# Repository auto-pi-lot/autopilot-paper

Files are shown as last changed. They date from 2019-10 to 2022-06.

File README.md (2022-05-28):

# SaundersWehr-Autopilot2019
Manuscript for Autopilot: https://www.biorxiv.org/content/10.1101/807693v1

# Building

The document is written with [tectonic](https://tectonic-typesetting.github.io/book/latest/). From the `autopilot` directory or any of its subdirectories, to build the document, run 

```bash
tectonic -X build 
```

The built document will then be located in [`autopilot/build/autopilot_v2/autopilot_v2.pdf`](autopilot/build/autopilot_v2/autopilot_v2.pdf).

**Safety Note:** To highlight the code, examples, we use [minted](http://tug.ctan.org/macros/latex/contrib/minted/minted.pdf), which requires the `shell_escape` option (specified in `Tectonic.toml`), which has the potential to run arbitrary code on your computer (we didn't purposely bundle any malware in the document).

See the blog post ["A Halfway Decent LaTeX Writing Setup"](https://jon-e.net/blog/2022/04/16/a-halfway-decent-latex-setup/) for further details and some nice QoL ideas for writing with LaTeX.

## Requirements

To compile the document, you will need

* [tectonic](https://tectonic-typesetting.github.io/book/latest/)
* [pygments](https://pygments.org/)

The fonts used in the document are mostly embedded within the .pdfs when relevant, and the open source fonts have been included in the repository, but to modify any of the source materials, you will need these fonts:

* [EB Garamond](http://www.georgduffner.at/ebgaramond/) - Bold, Italic, Regular - main body font (packaged in [`autopilot/src/garamond`](autopilot/src/garamond))
* [Fedra Mono](https://www.typotheque.com/fonts/fedra_mono) - Bold, Book, Light, Medium, Normal - Figure annotations
* [Fedra Sans Std](https://www.typotheque.com/fonts/fedra_sans) - Bold, Book, Medium, Normal, Condensed Bold, Condensed Medium - Figure axes, figure text.
* [Fira Code](https://github.com/tonsky/FiraCode) - Bold, Retina - In-text code (packaged in [`autopilot/src/fira`](autopilot/src/fira))
* [FontAwesome](https://ctan.org/pkg/fontawesome5) - Some glyphs.
* Loaded by [tufte-latex](https://github.com/Tufte-LaTeX/tufte-latex)
	* Bera Sans - Bold, Roman
	* Menlo - Regular
	* Nimbus Sans
	* PazoMath

# Document Structure

## `autopilot/`

The built document is in `autopilot/build`, and the document source is in `autopilot/src`. The `Tectonic.toml` file configures the build.

The main document text is written with:

* `_preamble.tex` - header material that defines styles, loads packages, etc.
* `autopilot.tex` - Index file that uses `\input` to combine the sections
* `sections/` - Each section is split up into multiple files within subfolders that correspond to the chapters of the paper:
	* `introduction`
	* `design`
	* `structure` - Program AStructure
	* `tests`
	* `conclusion` - Limitations and Future Directions, Glossary
* `_postamble.tex` - Document conclusion stuff.

The remaining files and folders in `src`:

* `autopilot.bib` - Bibliography for the paper exported from Zotero with Better BibTeX
* `version.tex` - A version hash that is included in the title page of the document, generated from a git hook (`.git/hooks/post-commit`).
* `figures`: The figures for the paper. Most are vectors stored as editable `.pdf` files with the flag to retain Illustrator editing features. All figures, including many not included in the first version and removed in the second version, are there. Figures containing data were mostly generated in R using [ggplot2](https://ggplot2.tidyverse.org/) and then styled (without changing the data itself) in Illustrator.
* `fira` and `garamond`: Fonts described above
* `styles`: The document style is a modified version of [tufte-latex](https://github.com/Tufte-LaTeX/tufte-latex). The source is admittedly extremely messy, I sort of hate LaTeX.
* `todo`: a separate todo document used in preparation of v2, kept for the sake of provenance.

## `code/`

The code that analyzed the data and generated the figures. Code for running the tests can be found in the autopilot paper plugin ([wiki](https://wiki.auto-pi-lot.com/index.php/Plugin:Autopilot_Paper), [repo](https://github.com/auto-pi-lot/plugin-paper)).

## `data/`

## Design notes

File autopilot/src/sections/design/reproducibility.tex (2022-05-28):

%!TEX root=../../autopilot.tex
\section{Reproducibility}
\label{sec:reproducibility}

We take a broad view on reproducibility: including not only the ability to share data and recreate experiments, but also integrating into a broader ecosystem of tools that reduces labor duplication and encourages sharing and organizing technical knowledge. For us, reproducibility means building a set of tools that make every experiment and every technique available to anyone, anywhere.

\subsection{Standardized task descriptions}

\begin{marginfigure}[-2cm]

\caption{\textbf{"Minor" details have major effects.} Proportion of mice (each point, n=4) that were successful learning the first stage of the speech task described in \citep{saundersMiceCanLearn2019} across 10 behavior boxes with variable reward sizes. A $2 \mu L$ difference in reward size had a surprisingly large effect on success rate.}
\label{fig:calibration}
\end{marginfigure}

The implementation and fine details of a behavioral experiment matter. Seemingly trivial details like milliseconds of delay between trial phases and microliters of reward volume can be the difference between a successful and unsuccessful task (Figure \ref{fig:calibration}). \textit{Reporting} those details can thus be the difference between a reproducible and unreproducible result.  Researchers also often use "auxiliary" logic in tasks---such as methods for correcting response bias---that are never completely neutral for the interpretation of results. These too can be easily omitted due to brevity or memory in plain-English descriptions of a task, such as those found in Methods sections. Even if all details of an experiment were faithfully reported, the balkanization of behavioral software into systems peculiar to each lab (or even to individuals within a lab) makes actually performing a replication of a behavior result expensive and technically challenging. Widespread use of experimental tools that are not explicitly designed to preserve every detail of their operation presents a formidable barrier to rigorous and reproducible science\citep{wallReliabilityStartsExperimental2019}.

%
\begin{marginfigure}[1.5cm]
\begin{minted}[frame=lines,fontsize=\small]{json}
{
"step_name"    : "tone_discrim",
"task_type"    : "2AFC",
"bias_mode"    : 0,
"punish_sound" : false,
"stim" : {
  "sounds" : {
    "L": {
      "duration"  : 100,
      "frequency" : 10000,
      "type"      : "tone",
      "amplitude" : 0.01},
    "R": {"...":"..."}}},
"reward": {
  "type"     : "volume",
  "volume"   : 20},
"graduation" : {
    "type"      : "accuracy",
    "threshold" : 0.75,
    "window"    : 400},
}
\end{minted}
\caption{Task parameters are stored as portable JSON, formatting has been abbreviated for clarity.}
\label{fig:params}
\end{marginfigure}%
%
%
Autopilot splits experiments into a) the \textbf{code} that runs the experiment, which is intended to be standardized and shared across implementations, and b) the \textbf{parameters} (Figure \ref{fig:params}) that define your particular experiment and system configuration. For example, two-alternative forced choice tasks have a shared structure regardless of the stimulus modality, but only your task plays pitch-shifted national anthems. This division of labor, combined with Autopilot's structured plugin system, help avoid the ubiquitous problem of rig-specific code and hard-coded variables making experimental code only useful on the single rig it was designed for --- enabling the possibility of a shared library of tasks as described in \hyperref[sec:expansion]{section \ref{sec:expansion}}%

The practice of reporting exactly the parameter description used by the software to run the experiment removes any chance for incompleteness in reporting. Because all task parameters are included in the produced data files, tasks are fully portable and can be reimplemented exactly by anyone that has comparable hardware to yours. 

\subsection{Self-Documenting Data}
\label{sec:data}

\begin{marginfigure}[1.5cm]

\caption{Example data structure. All information necessary to reconstruct an experiment is automatically stored in a human-readable HDF5 file.}
\label{fig:datastx}
\end{marginfigure}

A major goal of the open science movement is to normalize publishing well documented and clearly formatted data alongside every paper. Typically, data are acquired and stored in formats that are lab-idiosyncratic or ad-hoc, which, over time, sprout entire software libraries needed just to clean and analyze it. Idiosyncratic data formats hinder collaboration within and between labs as the same cleaning and analysis operations gain multiple, mututally incompatible implementations, duplicating labor and multiplying opportunities for difficult to diagnose bugs. Over time these data formats and their associated analysis libraries can mutate and become incompatible with prior versions, rendering years of work inaccessible or uninterpretable. In one worst-case scenario, the cleaning process unearths some critically missing information about the experiment, requiring awkward caveats in the Methods section or months of extra work redoing it. In another, the missing information or bugs in analysis code are never discovered, polluting scientific literature with inaccuracies. 

The best way to make data publishable is to avoid cleaning data altogether and \textit{design good data hygiene practices into the data acquisition process.} Autopilot automatically stores all the information required to fully reconstruct an experiment, including any changes in task parameters or code version that happen throughout training as the task is refined.

Autopilot data is stored in \href{https://support.hdfgroup.org/HDF5/whatishdf5.html}{HDF5} files, a hierarchical, high-performance file format. HDF5 files support metadata throughout the file hierarchy, allowing annotations to natively accompany data. Because HDF5 files can store nearly all commonly used data types, data from all collection modalities---trialwise behavioral data, continuous electrophysiological data, imaging data, etc.---can be stored together from the time of its acquisition. Data is always stored with the full conditions of its collection, and is ready to analyze and publish immediately (Figure \ref{fig:datastx}). No Autopilot-specific scripts are needed to import data into your analysis tool of choice---anything that can read HDF5 files can read Autopilot data\sidenote{Though our \texttt{Subject} class provides a simplified interface to access and manipulate Autopilot data}. 

As of v0.5.0, we have built a formal data modeling system into Autopilot, allowing for unified declaration of data for experimental subjects, task parameters, and resulting data with verifiable typing and human-readable annotations. These abstract data models can be used with multiple storage interfaces, paving the way for export to, for example, the Neurodata Without Borders standard\citep{rubelNWBAccessibleData2019}, further enabling Autopilot data to be immediately incorporated into existing processing pipelines (see section \ref{sec:datamodel}).

\subsection{Testing \& Continuous Integration}

Open-source scientific software does away with prior limitations to access and inspection imposed by proprietary tools. It also exposes the research process to bugs in software written by semi-amateurs that can yield errors in the resulting data, analysis, and interpretation\citep{soergelRampantSoftwareErrors2015,eklundClusterFailureWhy2016a,bhandarineupaneCharacterizationLeptazolinesPolar2019,millerScientistNightmareSoftware2006}. Autopilot tries to bring best practices in software development to experimental software, including a set of automated tests for continuous integration. 

We are still formalizing our contribution process, and our tests are still far from achieving full coverage\sidenote[][-3.25cm]{Coverage statistics for Autopilot are available on coveralls.io at \url{https://coveralls.io/github/auto-pi-lot/autopilot}}, but we currently require tests and documentation for all new code added to the library. Writing good tests is hard, and we are in the process of building a set of hardware simulators and test fixtures to ease contribution.  

Tests are effectively provable statements about how a program functions (Figure \ref{fig:tests}), which are particularly important for a library that aspires to be baseline lab infrastructure like Autopilot. Tests make it possible to use and contribute to the library with confidence: all tests are run on every commit, making it possible to determine if some new contribution breaks existing code without manually reading and testing every line. As we work to complete our test coverage, we hope to provide researchers with a tool that they can trust and elevates the verifiability of scientific results at large.

\begin{marginfigure}[-7cm]
\begin{minted}[frame=lines,fontsize=\small]{python}
def test_set_gpio():
    """
    The `set` method of a Digital_Out
    object sets the pin state
    """
    pin = Digital_Out(pin=17)

    # Turn GPIO pin on
    pin.set(True)
    assert pin.state == True

    # Turn GPIO pin off
    pin.set(False)
    assert pin.state == False
\end{minted}
\caption{A test like \texttt{test\_set\_gpio} is a provable statement about the functionality of a program, in this case that "the \texttt{Digital\_Out.set()} method sets the state of a GPIO pin."}
\label{fig:tests}
\end{marginfigure}

\subsection{Expense}
\label{sec:expense}

Autopilot is an order of magnitude less expensive than comparable behavioral systems (Table \ref{tab:cost}). We think the expense of a system is important for two reasons: scientific equity and statistical power. 

The distribution of scientific funding is highly skewed, with a large proportion of research funding concentrated in relatively few labs\citep{katzBiomedicalEliteInequality2017}. Lower research costs benefit all scientists, but lower instrumentation costs directly increase the accessibility of state-of-the-art experiments to labs with less funding. Since well-funded labs also tend to be concentrated at a few (well-funded) institutions, lower research costs also broaden the base of scientists outside traditional research institutions that can stay at the cutting edge\citep{ashkenasEvenAffirmativeAction2017,clausetSystematicInequalityHierarchy2015,pearceExpandingEquitableAccess2019}.
\clearpage%
%
\begin{marginfigure}[0.5cm]

\caption{When comparing a value across groups, eg. a genetic knockout vs. wildtype, even a modest intra-animal (or, more generally, intra-cluster) correlation (ICC) causes the false positive rate to be far above the nominal $\alpha = 0.05$. Shown are false positive rates for simulated data with various numbers of "cells" recorded for comparisons between two groups of 5 animals each with a real effect size of 0. We note that 741 simultaneously recorded cells were reported in \citep{junFullyIntegratedSilicon2017} and a mean ICC of 0.19 across 18 neuroscientific datasets was reported in \citep{aartsSolutionDependencyUsing2014}}
\label{fig:icc}
\end{marginfigure}%
%
Neuroscience also stands to benefit from the lessons learned from the replication crisis in Psychology\citep{shroutPsychologyScienceKnowledge2018}. In neuroscience, underpowered experiments are the rule, rather than the exception\citep{buttonPowerFailureWhy2013}. Statistical power in neuroscience is arguably even worse than it appears, because large numbers of observations (eg. neural recordings) from a small number of animals are typically pooled, ignoring the nested structure of observations collected within individual animals. Increasing the number of cells recorded from a small number of animals dramatically increases the likelihood of Type I errors (Figure \ref{fig:icc})---indeed, for values of within-animal correlation typical of neuroscientific data, high numbers of observations make Type I errors more likely than not\citep{aartsSolutionDependencyUsing2014}. For this reason, perhaps paradoxically, recent technical advances in multiphoton imaging and silicon-probe recordings will actually make statistical rigor in neuroscience \textit{worse} if we don't use analyses that account for the multilevel structure of the data and correspondingly record from the increased number of animals that they require.

Although the expense of multi-photon imaging and high-density electrophysiology will always impose an experimental bottleneck, behavioral training time is often the greater determinant of study sample size. Typical behavioral experiments require daily training sessions often carried out over weeks and months, while far fewer imaging or electrophysiology sessions are carried out per animal.  Training large cohorts of animals in parallel is thus the necessary basis of a well-powered imaging or electrophysiology experiment.

\begin{table}
\caption{\textbf{Cost for Basic 2AFC System}\\
\noindent"Nosepoke" includes a solenoid valve, IR sensor, water tube, LED, housing, and any necessary driver PCBs. For PyControl and Autopilot, we included the cost of one \href{https://wiki.auto-pi-lot.com/index.php/Lee_LHDA0531115H}{Lee LHDA0531115H} solenoid valve per nosepoke (\$63.35). For PyControl, we estimated a typical USB hub with 5 ports to control 5 pyControl systems from one computer. We note that the Bpod and PyControl systems both include cost of assembly for the control CPUs and nosepokes, but also that Autopilot does not require assembly for its control CPU and its default nosepoke is a snap-together 3D printed part and PCB without surface mounted components that can be assembled by an amateur in roughly half an hour.}
\label{tab:cost}
\noindent\begin{tabularx}{\linewidth}{XRRR}\toprule
& Autopilot & pyControl & Bpod  \\
\midrule
Behavior CPU & 
\href{https://www.adafruit.com/product/4292}{\texttt{\$45}} & 
\href{https://open-ephys.org/pycontrol/pycontrol}{\texttt{\$270}} & 
\href{https://sanworks.io/shop/viewproduct?productID=1024}{\texttt{\$925}}\\
Nosepoke (3x) & 
\texttt{\$216} & 
\href{http://www.open-ephys.org/store/pycontrol-peripherals}{\texttt{\$369}} & 
\href{https://sanworks.io/shop/viewproduct?productID=1009}{\texttt{\$810}} \\
\textbf{Total for One} & 
\textbf{\texttt{\$261}} & 
\textbf{\texttt{\$639}} & 
\textbf{\texttt{\$1735}}\\
\midrule
Five Systems & 
\texttt{\$1305} & 
\texttt{\$3195} & 
\texttt{\$8675} \\
Host CPU(s) & 
\texttt{\$1000} & 
\texttt{\$1000} & 
\texttt{\$5000} \\
\textbf{Total for Five} & 
\textbf{\texttt{\$2305}} & 
\textbf{\texttt{\$4195}} & 
\textbf{\texttt{\$13625}} \\
\midrule
\textbf{Total for Ten} & 
\textbf{\texttt{\$3610}} & 
\textbf{\texttt{\$8390}} & 
\textbf{\texttt{\$27350}} \\
\bottomrule
\end{tabularx}
\end{table}

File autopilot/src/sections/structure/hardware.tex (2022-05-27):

%!TEX root=../../autopilot.tex
\section{Hardware}
\label{sec:hardware}

The Raspberry Pi can interface with nearly all common hardware, and has an \href{https://www.raspberrypi.org/help/}{extensive collection} of \href{https://elinux.org/RPi_Guides}{guides}, \href{https://elinux.org/RPi_Tutorials}{tutorials}, and an active \href{https://www.raspberrypi.org/forums/}{forum} to support users implementing new hardware. There is also an enormous amount of existing hardware for the Raspberry Pi, including \href{https://www.hifiberry.com/}{sound cards}, \href{https://www.adafruit.com/product/2348}{motor controllers}, \href{https://www.digikey.com/product-detail/en/raspberry-pi/SENSE-HAT/1690-1013-ND/6196429}{sensor arrays}, \href{https://www.seeedstudio.com/Raspberry-Pi-High-Precision-AD-DA-Board-p-2765.html}{ADC/DACs}, and \href{https://www.digikey.com/product-detail/en/pimoroni-ltd/PIM369/1778-1221-ND/9521981}{touchscreen displays}, largely eliminating the need for a separate ecosystem of purpose-built hardware (Table \ref{tab:periphs}). 

\begin{margintable}[-0.75cm]
\caption{
\textbf{Cost of common peripherals.} The native hardware of the Raspberry Pi, low-level hardware control of Autopilot, and availability of inexpensive off-the-shelf components compatible with the raspi make most custom-built peripherals unnecessary.}
\label{tab:periphs}
\noindent\begin{tabularx}{\linewidth}{Rll}
\toprule
\textbf{Device} & Raspi & Bpod \\
\midrule
HiFiBerry DAC2 Pro & \href{https://www.hifiberry.com/shop/boards/hifiberry-dac2-pro/}{\$45} &  \href{https://sanworks.io/shop/viewproduct?productID=1032}{\$445}\\
ADC & \href{https://thepihut.com/products/high-precision-adc-hat-for-raspberry-pi-10-channel-32-bit}{\$30} & \href{https://sanworks.io/shop/viewproduct?productID=1021}{\$495}\\
I2C & \$0 & \href{https://sanworks.io/shop/viewproduct?productID=1019}{\$225} \\
Ethernet & \$0 & \href{https://sanworks.io/shop/viewproduct?productID=1025}{\$285} \\
Rotary Encoder & \$0 &  \href{https://sanworks.io/shop/viewproduct?productID=1022}{\$145}\\
\bottomrule
\end{tabularx}
\end{margintable}

\begin{marginfigure}[0cm]
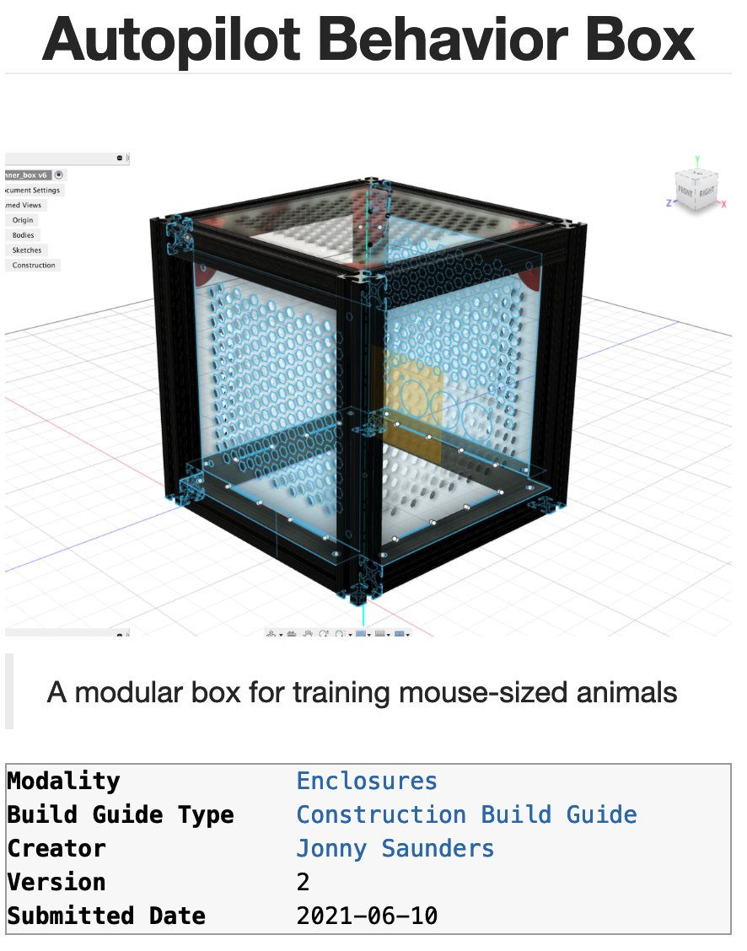
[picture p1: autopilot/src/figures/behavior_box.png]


\caption{Two examples of parts with assembly guides available on the autopilot wiki: A modular \href{https://wiki.auto-pi-lot.com/index.php/Autopilot_Behavior_Box}{behavior box} with magnetic snap-in panels (top), and a \href{https://wiki.auto-pi-lot.com/index.php/Autopilot_Tripoke}{three-nosepoke panel} (bottom).}
\label{fig:pokeport}
\end{marginfigure}%

Autopilot controls hardware with an extensible inheritance hierarchy of Python classes intended to be built into a library of hardware controllers analogously to tasks. Autopilot uses \href{http://abyz.me.uk/rpi/pigpio/}{pigpio} to interact with its GPIO pins, giving Autopilot $5 \mu s$ measurement precision and enabling protocols that require high precision (such as Serial, PWM, and I2C) for nearly all of the pins.  Currently, Autopilot also has a family of objects to control cameras (both the \href{https://docs.auto-pi-lot.com/en/latest/hardware/cameras.html\#autopilot.hardware.cameras.PiCamera}{Raspberry Pi Camera} and \href{https://docs.auto-pi-lot.com/en/latest/hardware/cameras.html\#autopilot.hardware.cameras.Camera_Spinnaker}{high-speed GENICAM-compliant} cameras), i2c-based \href{https://docs.auto-pi-lot.com/en/latest/hardware/i2c.html\#autopilot.hardware.i2c.I2C_9DOF}{motion} and \href{https://docs.auto-pi-lot.com/en/latest/hardware/i2c.html\#autopilot.hardware.i2c.MLX90640}{heat} sensors, and \href{https://docs.auto-pi-lot.com/en/latest/hardware/usb.html\#autopilot.hardware.usb.Wheel}{USB mice}.  In the \hyperref[sec:future]{future} we intend to improve performance further by replacing time-critical hardware operations with low-level interfaces written in Rust.

\begin{table}[b]
\caption[][0cm]{Specifications of reviewed behavior hardware. BPod's state machine uses the Teensy 3.6 microcontroller, and PyControl uses the Micropython Pyboard.}
\label{hwtab}
\begin{tabularx}{\linewidth}{Rp{3.5cm}p{2cm}p{2cm}}\toprule
& \href{https://www.raspberrypi.org/products/raspberry-pi-4-model-b/specifications/}{\textbf{Raspberry Pi 4B}} & \href{https://www.pjrc.com/teensy/techspecs.html}{\textbf{Teensy 3.6}} & \href{https://micropython.org/}{\textbf{pyboard}}\\
\midrule
CPU Clock & 1.5GHz & 180MHz & 168MHz \\
CPU Cores & 4 & 1 & 1 \\
Architecture & ARMv8-A, 64-bit & ARMv7 32-bit & ARMv7 32-bit \\
RAM Size & 2, 4, or 8GB & 256KB & 192KB\\
Storage & MicroSD (any size) & 1024KB & 1024KB \\
GPU & Broadcom VideoCore VI & \textcolor{red}{---} & \textcolor{red}{---} \\
GPIO Pins & 40 & 58 & 29 \\
USB Ports & 2x USB 2.0, 2x USB 3.0  & 2x USB 2.0 & 1x USB 2.0 \\
Ethernet & 1Gbps & 100Mbps & \textcolor{red}{---} \\
WiFi & 2.4/5 GHz b/g/n/ac & \textcolor{red}{---} & \textcolor{red}{---} \\
Camera & 15-pin Serial Interface & \textcolor{red}{---} & \textcolor{red}{---} \\
Bluetooth & \checkmark & \textcolor{red}{---} & \textcolor{red}{---} \\
\end{tabularx}
\end{table}

To organize and make available the vast amount of contextual knowledge needed to build and use experimental hardware, we have made a densely linked and publicly editable \href{https://wiki.auto-pi-lot.com/index.php/Autopilot_Wiki}{semantic wiki}. The Autopilot wiki contains, among others, reference information for \href{https://wiki.auto-pi-lot.com/index.php/Parts}{off-the-shelf parts}, schematics for \href{https://wiki.auto-pi-lot.com/index.php/2D_CAD}{2D} and \href{https://wiki.auto-pi-lot.com/index.php/3D_CAD}{3D}-printable components, and \href{https://wiki.auto-pi-lot.com/index.php/Guides}{guides} for building experimental apparatuses and custom parts. The wiki combines unrestrictive freeform editing with structured, computer-readable \href{https://www.semantic-mediawiki.org/wiki/Semantic_MediaWiki}{semantic properties}, and we have defined a collection of \href{https://wiki.auto-pi-lot.com/index.php/Special:CategoryTree?target=Hardware&mode=categories&namespaces=&title=Special%3ACategoryTree}{schemas} for commonly documented items coupled with \href{https://wiki.auto-pi-lot.com/index.php/Special:Forms}{submission forms} for ease of use. For example, the wiki page for the \href{https://wiki.auto-pi-lot.com/index.php/Lee_LHDA0531115H}{Lee Company solenoid} we use has fields from a generic \href{https://wiki.auto-pi-lot.com/index.php/Category:Part}{Part} schema like a datasheet, price, and voltage, but also that it's a 3-way, normally-closed \href{https://wiki.auto-pi-lot.com/index.php/Category:Solenoid}{solenoid}. 

The wiki's blend of structure and freedom breaks apart typically monolithic hardware documentation into a collaborative, multimodal technical knowledge graph. Autopilot can access the wiki through its \href{https://docs.auto-pi-lot.com/en/latest/guide/plugins.html\#the-wiki-api}{API}, and we intend to tighten their integration over time, including automatic configurations for common parts, usage and longevity benchmarks, detecting mutually incompatible parts, and automatically resolving any additional plugins or dependencies needed to use a part.

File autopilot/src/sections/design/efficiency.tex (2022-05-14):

%!TEX root=../../autopilot.tex
\section{Efficiency}
\label{sec:efficiency}

Though it is a single board, the Raspberry Pi operates more like a computer than a microcontroller. It most commonly runs a custom Linux distribution, Raspbian, allowing Autopilot to use Python across the whole system. Using an interpreted language like Python running on Linux has inherent performance drawbacks compared to compiled languages running on embedded microprocessors. In practice these drawbacks are less profound than they appear on paper: Python's overhead is negligible on modern processors\sidenote{and improvements to CPython in \href{https://docs.python.org/3.11/whatsnew/3.11.html\#faster-cpython}{Python 3.11} and onwards will bring overhead close to zero\citep{andersonGuidoVanRossum2021}}, jitter and performance can be improved by wrapping \hyperref[sec:lowlevel]{compiled code}, etc. While we view the gain in accessibility and extensibility of a widely used high-level language like Python as outweighing potential performance gains from using a compiled language, Autopilot is nevertheless designed to maximize computational efficiency.

\subsection{Concurrency}

\begin{marginfigure}[2cm]

\caption{A single-threaded program executes all operations sequentially, using a single process and cpu core.}
\label{fig:singlethread}
\end{marginfigure}

Most behavioral software is single-threaded (Figure \ref{fig:singlethread}), meaning the program will only perform a single operation at a time. If the program is busy or waiting for an input, other operations are blocked until it is finished.

Autopilot distributes computation across multiple processes and threads to take advantage of the Raspberry Pi's four CPU cores. Most operations in Autopilot are executed in \textbf{threads}. Specifically, Autopilot spawns separate threads to process messages and events, an architecture described more fully in \hyperref[sec:networking]{section \ref*{sec:networking}}. Threading does not offer true concurrency\sidenote{See David Beazley's  \href{http://www.dabeaz.com/python/UnderstandingGIL.pdf}{`Understanding the Global Interpreter Lock'} and associated \href{http://www.dabeaz.com/GIL/gilvis/index.html}{visualizations}.}, but does allow Python to distribute computational time between operations so that, for example, waiting for an event does not block the rest of the program, and events are not missed because the program is busy (Figure \ref{fig:multithread}).

\begin{marginfigure}[0.25cm]

\caption{A multi-threaded program divides computation time of a single process and cpu core across multiple operations so that, for example, waiting for input doesn't block other operations.}
\label{fig:multithread}
\end{marginfigure}

Critical operations that are computationally intensive or cannot be interrupted are given their own dedicated \textbf{processes}. Linux allows individual cores of a processor to be reserved for single processes, so individual Raspberry Pis are capable of running four truly parallel processing streams. For example, all Raspberry Pis in an Autopilot swarm create a messaging client to handle communication between devices which runs on its own processor core so no messages are missed. Similarly, if an experiment requires sound delivery, a realtime \hyperref[sec:stim]{sound engine} in a separate process (Figure \ref{fig:multiprocess}) also runs on its own core.

\begin{marginfigure}[0.1cm]
 
 \caption{A multi-process program is truly concurrent, allowing multiple cpu cores to operate in parallel.}
 \label{fig:multiprocess}
\end{marginfigure}

Since even moderately complex experiments can consume more resources than are available on a single processor, the topmost layer of concurrency in Autopilot is to use additional \textbf{computers}. Autopilot uses the Raspberry Pi as a low-cost hardware controller, but only its GPIO control system is unique to them: the rest of the code can be used on any type of computer, so computationally expensive or GPU-intensive operations can be offloaded to any number of high performance machines. Computers divide labor \textit{autonomously} (see \ref{sec:message_handling} and \ref{sec:agents} ), so for example one computer running a task can send and receive messages from another running the GUI and plots, but does not \textit{depend} on that input as it would in a system that couples a microcontroller with a managing computer. The ability to coordinate multiple, autonomous computers with heterogeneous responsibilities and capabilities in a shared task is Autopilot's definitive design decision.

\subsection{Leveraging Low-Level Libraries}
\label{sec:lowlevel}

\begin{margintable}[1.85cm]
\caption{A few libraries Autopilot uses}
\label{tab:libraries}
\noindent\begin{tabularx}{\linewidth}{rX}
\toprule
 \textbf{\href{http://jackaudio.org/}{jack}} & realtime audio \\
 \textbf{\href{http://abyz.me.uk/rpi/pigpio/index.html}{pigpio}} & GPIO control \\
 \textbf{\href{http://zeromq.org/}{ZeroMQ}} & networking \\
 \textbf{\href{https://www.qt.io/}{Qt}} & GUI \\
 \bottomrule
\end{tabularx}
\end{margintable}

Autopilot uses Python as a "glue" language, where it wraps and coordinates faster low-level compiled code\citep{vanrossumGlueItAll1998}.  
Performance-critical components of Autopilot are thin wrappers around fast C libraries (Table \ref{tab:libraries}). As Autopilot's API matures, we intend to replace any performance-limiting Python code like its sound server and networking operations with compiled code exposed to python with tools like the C Foreign Function Interface (\href{https://cffi.readthedocs.io/en/latest/index.html}{CFFI}).

Since Autopilot coordinates its low-level components in parallel rather putting everything inside one "main loop," Autopilot actually has \textit{better} temporal resolution than  single-threaded systems like Bpod or pyControl, despite the realtime nature of their dedicated processors (Table \ref{tab:precision}).

\begin{margintable}
\caption{Using pigpio as a dedicated I/O process gives autopilot greater measurement precision}
\label{tab:precision}
\noindent\begin{tabularx}{\linewidth}{rR}\toprule
& Precision \\
\midrule
Autopilot (\href{http://abyz.me.uk/rpi/pigpio/pigpiod.html}{pigpio}) & $5\mu s$ \\
\href{https://github.com/sanworks/Bpod_StateMachine_Firmware/blob/059d1e9195f5bb7d0d5cd7b33f56342eb5a3a55c/Dev/StateMachineFirmware/StateMachineFirmware.ino\#L196}{Bpod} & $100\mu s$ \\
\href{https://github.com/pyControl/code/blob/28cf5ea28ca2764aeea829eba148adfa5239254a/pyControl/framework.py\#L228}{pyControl} & $1000\mu s$ \\
\bottomrule
\end{tabularx}
\end{margintable}

\subsection{Caching}

Finite-state machines are only aware of the current state and the events that transition it to future states. They are thus incapable of exploiting the often predictable structure of behavioral tasks to precompute future states and precache stimuli. Further, to change task parameters between trials (eg. changing the rewarded side in a two-alternative forced-choice task), state machines need to be fully reconstructed and reuploaded to the device that runs them each time.

Autopilot precomputes and caches as much as possible. Rather than wait "inside" a state, Autopilot prepares each of the next possible events and saves them for immediate execution when the appropriate trigger is received. Static stimuli are prepared once at the beginning of a behavioral session and stored in memory. Before their presentation, they are buffered to minimize latency.

By providing full low-level documentation, we let researchers choose the balance between ease of use and performance themselves: it's possible to just call a sound's \texttt{\href{https://docs.auto-pi-lot.com/en/latest/stim/sound/base.html\#autopilot.stim.sound.base.Jack_Sound.play}{play()}} method, explicitly buffer it with its \texttt{\href{https://docs.auto-pi-lot.com/en/latest/stim/sound/base.html\#autopilot.stim.sound.base.Jack_Sound.buffer}{buffer()}} method, or generate samples on the fly with its \texttt{\href{https://docs.auto-pi-lot.com/en/latest/stim/sound/base.html\#autopilot.stim.sound.base.Jack_Sound.play_continuous}{play\_continuous()}} method. Similarly, messages can be sent with a networking node's \texttt{\href{https://docs.auto-pi-lot.com/en/latest/networking/node.html\#autopilot.networking.node.Net_Node.send}{send()}} method, or prepared beforehand by explicitly making a \texttt{\href{https://docs.auto-pi-lot.com/en/latest/networking/message.html\#autopilot.networking.message.Message}{Message}} and calling its \texttt{\href{https://docs.auto-pi-lot.com/en/latest/networking/message.html\#autopilot.networking.message.Message.serialize}{serialize()}} method.

\vspace{16pt}

Autopilot's efficient design lets it access the best of both worlds---the speed and responsiveness of compiled code on dedicated microprocessors and the accessibility and flexibility of interpreted code.

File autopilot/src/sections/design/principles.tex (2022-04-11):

%!TEX root=../../autopilot.tex
\newthought{Autopilot distributes experiments} across a network of Raspberry Pis,\sidenote{\href{https://www.raspberrypi.org/products/raspberry-pi-4-model-b/}{Raspberry Pi model 4B}, see \hyperref[hwtab]{Table \ref*{hwtab}}} a type of inexpensive single-board computer.

\vspace{12pt}

\textbf{Autopilot has three primary design principles:}

\begin{enumerate}
    \item \hyperref[sec:efficiency]{\textbf{Efficiency}} - Autopilot should minimize computational overhead and maximize use of hardware resources.
    \item \hyperref[sec:flexibility]{\textbf{Flexibility}} - Autopilot should be transparent in all its operations so that users can expand it to fit their existing or desired use-cases. Autopilot should provide clear points of modification and expansion to reduce local duplication of labor to compensate for its limitations.
    \item \hyperref[sec:reproducibility]{\textbf{Reproducibility}} - Autopilot should maximize system transparency and minimize the potential for the black-box of local reprogramming. Autopilot should maximize the information it stores about its operation as part of normal data collection.
\end{enumerate}

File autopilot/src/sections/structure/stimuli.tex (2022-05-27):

%!TEX root=../../autopilot.tex
\section{Stimuli}
\label{sec:stim}

\begin{marginfigure}[0.45cm]
\begin{pythoncode*}{
label= \texttt{An Autopilot Tone},
frame=lines,
linenos=false}

my_tone = sounds.Tone(
    frequency = 500,
    duration  = 200)
my_tone.play()
\end{pythoncode*}
\caption{Autopilot stimuli are parametrically defined and inherit all the playback logic that makes them easy to integrate in tasks}
\label{fig:tone}
\end{marginfigure}

A hardware object would control a speaker, whereas stimulus objects are the individual sounds that the speaker would play. Like tasks and hardware, Autopilot makes stimulus generation portable between users, and is released with a family of common sounds like tones, noises, and sounds from files. The logic of sound presentation is contained in an inherited metaclass, so to program a new stimulus a user only needs to describe how to generate it from its parameters (Figure \ref{fig:tone}).  Sound stimuli are better developed than visual stimuli as of v0.5.0, but we present a proof-of-concept visual experiment (Section \ref{sec:gonogo}) using \href{https://www.psychopy.org/}{psychopy}\citep{peircePsychoPy2ExperimentsBehavior2019}.

Autopilot controls the realtime audio server \href{http://jackaudio.org/}{jack} from an independent Python process that dumps samples directly into jack's buffer (Figure \ref{fig:soundpath}), giving it a trigger-to-playback latency very near the theoretical minimum (Section \ref{sec:soundlatency}). Sounds can be pre-buffered in memory or synthesized on demand to play continuous sounds. Because the realtime server is independent from the logic of sound synthesis and storage, stimuli can be controlled independently from different threads without interrupting audio or dropping frames.

\begin{marginfigure}[0cm]

\caption{Our sound server keeps audio samples buffered until a \texttt{.play()} method is called, and then dumps them directly into the jack audio daemon.}
\label{fig:soundpath}
\end{marginfigure}

We use the \href{https://www.hifiberry.com/shop/boards/hifiberry-amp2/}{Hifiberry Amp 2}, a combined sound card and amplifier, which is capable of 192kHz/24Bit audio playback. Autopilot and Jack can output to any sound hardware, however, including the builtin audio of the Raspberry Pi if fidelity isn't important. There are no external video cards for the Raspberry Pi 4b\sidenote[][0cm]{though the Raspberry Pi compute module has a \href{https://web.archive.org/web/20220506011247/https://www.jeffgeerling.com/blog/2020/external-gpus-and-raspberry-pi-compute-module-4}{PCI lane that supports GPUs}.}, but its embedded video card is capable of presenting video and visual stimuli (Section \ref{sec:gonogo}) especially if the other computationally demanding parts of the task are distributed to other Raspberry Pis (Section \ref{sec:topology}). If greater video performance is needed, Autopilot is capable of running on typical desktops as well as other single-board computers with GPUs (as we did with the Nvidia Jetson in \citep{kaneRealtimeLowlatencyClosedloop2020a}).

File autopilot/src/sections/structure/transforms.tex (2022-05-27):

%!TEX root=../../autopilot.tex
\section{Transforms}
\label{sec:transforms}

In v0.3.0, we introduced the \texttt{transform} module, a collection of tools for transforming data. The raw data off a sensor is often not in itself useful for performing an experiment: we want to compare it to some threshold, extract positions of objects in a video feed, and so on. Transforms are like building blocks, each performing some simple operation with a standard object structure, and then composed into a pipeline (Figure \ref{fig:transform_example}). Pipelines are portable, and can be created on the fly from a JSON representation of their arguments, so it's easy to offload expensive operations to a more capable machine for distributed realtime experimental control (See \citep{kaneRealtimeLowlatencyClosedloop2020a}). 

\begin{marginfigure}[-8cm]

\end{marginfigure}

\begin{marginfigure}[-3.5cm]
\begin{pythoncode*}{
label= \texttt{Transform - DLC Live!},
frame=lines,
linenos=false}
from autopilot import transform as t
# track points on a human body
dlc = t.image.DLC(
    model_zoo="full_human")
# select one of the knees
dlc += t.selection.DLCSlice(
    select="knee2")
# Test if it's in an ROI
dlc += t.logical.Condition(
    minimum=(0,0),
    maximum=(128,128))

# Process frames with the pipeline
# set pin High if knee2 in ROI
while True:
    pin.set(dlc.process(
        cam.q.get()))
\end{pythoncode*}
\caption{Transforms can be chained together (here with the in-place addition operator \texttt{+=}) to make pipelines that encapsulate the logical relationship between some input and a desired output. Here \texttt{pin} is a \href{https://docs.auto-pi-lot.com/en/latest/hardware/gpio.html\#autopilot.hardware.gpio.Digital_Out}{Digital\_Out} object, and \texttt{cam} is a \href{https://docs.auto-pi-lot.com/en/latest/hardware/cameras.html\#autopilot.hardware.cameras.PiCamera}{PiCamera} with \texttt{queue} enabled.}
\label{fig:transform_example}

\end{marginfigure}

In addition to computing derived values, we use transforms in a few ways, including

\begin{itemize}
\item \textbf{Bridging Hardware} --- Different hardware devices use different data types, units, and scales, so transforms can \href{https://docs.auto-pi-lot.com/en/latest/transform/units.html\#autopilot.transform.units.Rescale}{rescale} and convert values to make them compatible.
\item \textbf{Integrating External Tools} --- The number of exciting analytical tools for realtime experiments keep growing, but in practice they can be hard to use together. The transform module gives a scaffolding for writing wrappers around other tools and exposing them to each other in a shared framework, as we did with DeepLabCut-Live\citep{kaneRealtimeLowlatencyClosedloop2020a}, making closed-loop pose tracking available to the rest of Autopilot's ecosystem. We don't need to rally thousands of independent developers to agree to write their tools in a shared library, instead transforms make wrapping them easy.
\item \textbf{Extending Objects} --- Transforms can be used to augment existing objects and create new ones. For example, a \href{https://docs.auto-pi-lot.com/en/latest/hardware/i2c.html#autopilot.hardware.i2c.I2C_9DOF}{motion sensor} uses the \href{https://docs.auto-pi-lot.com/en/latest/transform/geometry.html\#autopilot.transform.geometry.Spheroid}{spheroid} transform to calibrate its accelerometer, and the \href{https://docs.auto-pi-lot.com/en/latest/transform/timeseries.html\#autopilot.transform.timeseries.Gammatone}{gammatone filter}\sidenote[][0.25cm]{a thin wrapper around \href{https://docs.scipy.org/doc/scipy/reference/generated/scipy.signal.gammatone.html}{scipy's \texttt{signal.gammatone}}} extends the \href{https://docs.auto-pi-lot.com/en/latest/stim/sound/sounds.html\#autopilot.stim.sound.sounds.Noise}{Noise} sound to make a gammatone \href{https://docs.auto-pi-lot.com/en/latest/stim/sound/sounds.html\#autopilot.stim.sound.sounds.Gammatone}{filtered noise} sound.
\end{itemize}

Like Tasks and Hardware, the transform module provides a scaffolding for writing reference implementations of algorithms commonly needed for realtime behavioral experiments. For example, neuroscientists often want to quickly measure a research subject's velocity or orientation, which is possible with inexpensive inertial motion sensors (IMUs), but since anything worth measuring will be swinging the sensor around with wild abandon the readings first need to be rotated back to a geocentric coordinate frame. Since the readings from an accelerometer are noisy, we found a few whitepapers describing using a Kalman filter for fusing the accelerometer and gyroscope data for a more accurate orientation estimate (\citep{abyarjooImplementingSensorFusion2015b,patonisFusionMethodCombining2018a}), but couldn't find an implementation. We \href{https://docs.auto-pi-lot.com/en/latest/_modules/autopilot/transform/geometry.html\#IMU_Orientation}{wrote one} and integrated it into the IMU class (Figure \ref{fig:imu}). Since it's an independent transform, it's available to anyone even if they use nothing else from Autopilot.

\begin{marginfigure}[-1.5cm]
\begin{pythoncode*}{
label=Geocentric Velocity,
frame=lines,
linenos=false
}
# rotate input in x and y
# by some pitch and roll
reorient = t.geometry.Rotate(
    dims='xy') 
# select the z axis
reorient += t.selection.Slice(
    select=2)
# remove gravity
reorient += t.math.Add(
    -9.8)

# using I2C_9DOF...
angle = imu.rotation
z_accel = reorient.process(
    imu._acceleration, angle)
\end{pythoncode*}
\caption{Using the \href{https://docs.auto-pi-lot.com/en/latest/_modules/autopilot/transform/geometry.html\#IMU_Orientation}{IMU\_Orientation} transform built into the IMU's \texttt{rotation} property, a processing chain to reorient the accelerometer reading and subtract gravity for geocentric z-axis acceleration.}
\label{fig:imu}
\end{marginfigure} 

Transforms were made to be composed, so we broke it into independent sub-operations: A \href{https://docs.auto-pi-lot.com/en/latest/transform/timeseries.html\#autopilot.transform.timeseries.Kalman}{Kalman} filter, \href{https://docs.auto-pi-lot.com/en/latest/transform/geometry.html\#autopilot.transform.geometry.Rotate}{rotation}, and a \href{https://docs.auto-pi-lot.com/en/latest/transform/geometry.html\#autopilot.transform.geometry.Spheroid}{spheroid correction} to calibrate accelerometers. Then we combined it with the DLC-Live transform for a fast but accurate motion estimate from position, velocity, and acceleration measurements from three independent sensors. Since each step of the transformation is exposed in a clean API, it was straightforward to \href{https://github.com/auto-pi-lot/autopilot-plugin-parallax/blob/759dbb382b90a99f71edf5070772ac18555b67dd/kalman\_position.py}{extend the Kalman filter} to accomodate the the wildly different sampling rates of the camera and IMU. It's still got its quirks, but that's the purpose of plugins --- to make the code \href{https://wiki.auto-pi-lot.com/index.php/Plugin:Parallax}{available and documented} without formally integrating it in the library. 

\clearpage

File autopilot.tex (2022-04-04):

% !TEX options=--shell-escape
\documentclass[nohyper, justified, notitlepage, marginals=raggedright,twoside=false,debug]{tufte-autopilot}

%% Package imports
\usepackage{microtype}
\usepackage{amsmath}
\usepackage{booktabs}
\usepackage{xspace}
\usepackage{units}
\usepackage{makeidx}
\usepackage[framemethod=tikz]{mdframed}% http://ctan.org/pkg/mdframed
\usepackage{lipsum}
\usepackage{listings}
\usepackage{minted}
%\usepackage[usenames, svgnames]{xcolor}
\usepackage[colorlinks = true,
            urlcolor = DarkOrchid,
            citecolor = DarkOrchid,
            backref= section]{hyperref}
\usepackage{tikz}
\usepackage{verbatim}
\usepackage{tabularx}
\usepackage{enumitem} % pause itemize env
\usepackage[font=footnotesize, labelfont=bf]{caption}
\usepackage{ulem}     % strikeouts
%\usepackage[english]{babel}
\usepackage[autostyle, english=american]{csquotes} % styling smart quotes
\usepackage[titletoc]{appendix} % add appendices
%\usepackage{scrextend}
%\usepackage{etoolbox}
%\usepackage[toc, automake=true]{glossaries}
\usepackage{listliketab}
%\usepackage{authblk}
%\usepackage{abstract} % to get saythanks
\usepackage{ fontawesome }

\usetikzlibrary{tikzmark}
\usetikzlibrary{calc}
\usetikzlibrary{positioning}
\usetikzlibrary{decorations.pathreplacing}

%% Imports with customizations
% For graphics / images
\usepackage{graphicx}
\setkeys{Gin}{width=\linewidth,totalheight=\textheight,keepaspectratio}
\graphicspath{{graphics/}}

\usepackage{fancyvrb}
\fvset{fontsize=\normalsize}

\titlespacing*{\chapter}{0pt}{-10pt}{0pt}
%\titlespacing{\section}{0pt}{30pt}{0pt}

%% Import extra shit from overleaf doc - see what's necessary.
\usepackage{extra}

%%%%%%%%%%%%%%%%%%%%%%%%%%%%%
%%%%%%%%%%%%%%%%%%%%%%%%%%%%%

% adding colon to appendix
% don't ask me what's going on
% https://tex.stackexchange.com/a/201328
%\apptocmd{\appendices}{\apptocmd{\thechapter}{: }{}{}}{}{}

\renewcommand\appendixname{Appendix: }

% restyle captions
\setcaptionfont{\footnotesize\raggedright}
\setsidenotefont{\footnotesize}
\setmarginnotefont{\footnotesize}

% style captions, including adding more space after figures
\captionsetup{justification=raggedright, singlelinecheck=false}
%\captionsetup[figure]{belowskip=24pt, position=below}
%\captionsetup[table]{aboveskip=12pt, position=above}

\setlength{\abovecaptionskip}{3pt plus 2pt minus 3pt}

% format smart quotes
\MakeOuterQuote{"}

% Styling for code blocks
\usemintedstyle{colorful}
%\setminted{fontsize=\small}

% set escape chars in listing
\lstset{
    language = Python,
    breaklines=true,
    escapeinside=||
}

\definecolor{aliceblue}{rgb}{0.98, 0.98, 0.99}

%\renewcommand{\theFancyVerbLine}{%
%\textt\small\arabic{FancyVerbLine}}

% right aligned tabularx
\newcolumntype{R}{>{\raggedleft\arraybackslash}X}

\setcounter{secnumdepth}{1}
\setcounter{tocdepth}{1}

\newminted{python}{linenos=true,
               frame=single,
               framerule = 1pt,
               labelposition = topline,
               bgcolor=aliceblue,
               escapeinside=||}

\newminted{matlab}{linenos=true,
frame=single,
framerule = 1pt,
labelposition = topline,
bgcolor=aliceblue,
escapeinside=||}

\geometry{
%  left=1in, % left margin
%  textwidth=27pc, % main text block
  marginparsep=1pc, % gutter between main text block and margin notes
%  marginparwidth=12pc % width of margin notes
}

\newenvironment{abstract}{%
\vspace{1em}
\begin{mdframed}[
     linewidth=1pt,
     linecolor=black,
     bottomline=false,topline=false,rightline=false,
     innerrightmargin=0pt,innertopmargin=0pt,innerbottommargin=0pt,
     innerleftmargin=1em,% Distance between vertical rule & proof content
     skipabove=.5\baselineskip
   ]
}{%
\end{mdframed}
}

\newenvironment{thintab}%
{\begin{itemize}%
\setlength{\itemsep}{0pt}%
\setlength{\parskip}{0pt}}%
{\end{itemize}}

% Define symbols
% https://tex.stackexchange.com/a/132790
\def\checkmark{\tikz\fill[scale=0.4](0,.35) -- (.25,0) -- (1,.7) -- (.25,.15) -- cycle;}

% Generates the index

% environment to center figures
\newcommand{\linkfigure}[3]{\begingroup
\setbox0=\hbox{}%
\parbox{\wd0}{\box0}\endgroup \hspace{6pt} \href{#3}{\sffamily\large\textcolor{red}{\allcaps{#2}}}}

\definecolor{RED}{HTML}{FF0000}
%%
% Book metadata
\title{Auto\textcolor{RED}{pi}lot\\
\large Automating behavioral experiments with lots of Raspberry Pis}
\author{JONNY L. SAUNDERS, MICHAEL WEHR \href{mailto:wehr@uoregon.edu}{\faAt}}
% filthy hack putting the affiliations in the tufte-common.cls file. 
% goddamn hate latex.
% what in holy hell...

\begin{document}
% r.3 full title page
\maketitle%

\begin{abstract}

Neuroscience needs behavior, and behavioral experiments require the coordination of large numbers of heterogeneous hardware components and data streams. Currently available tools strongly limit the complexity and reproducibility of experiments. Here we introduce Autopilot, a complete,  open-source Python framework for behavioral neuroscience that distributes experiments over networked swarms of Raspberry Pis. Autopilot enables qualitatively greater experimental flexibility by allowing arbitrary numbers of hardware components to be combined in arbitrary experimental designs. Research is made reproducible by documenting all data and task design parameters in a human-readable and publishable format at the time of collection. Autopilot provides an order-of-magnitude performance improvement over existing tools while also being an order of magnitude less costly to implement. Autopilot's flexible, scalable architecture allows neuroscientists to design the next generation of experiments to investigate the behaving brain.

\end{abstract}%

\vspace{20pt}

\linkfigure{figures/autopilot_logo_small_notext.pdf}{Homepage}{https://auto-pi-lot.com} 

\linkfigure{figures/gh_logo.pdf}{Repository}{https://github.com/wehr-lab/autopilot}

\linkfigure{figures/question-circle-solid.pdf}{Documentation}{https://docs.auto-pi-lot.com}

%
% r.5 contents
\tableofcontents%
%
\mainmatter%
%
\chapter{Introduction}

\newthought{Animal behavior} experiments require precision and repetition, which can best be achieved by computer automation. The complexity of contemporary behavioral experiments, however, presents a stiff methodological challenge. For example, researchers might wish to measure pupil dilation\citep{reimerPupilFluctuationsTrack2016, reimerPupilFluctuationsTrack2016}, respiration\citep{parabuckiOdorConcentrationChange2019}, and running speed\citep{niellModulationVisualResponses2010}, while tracking the positions of body parts in 3 dimensions\citep{nathUsingDeepLabCut3D2019} and recording the activity of large ensembles of neurons\citep{junFullyIntegratedSilicon2017}, as subjects perform tasks with custom input devices such as a steering wheel\citep{burgessHighYieldMethodsAccurate2017} while immersed in virtual reality environments using stimuli synthesized in real time\citep{thurleyVirtualRealitySystems2017,chambersOnlineStimulusOptimization2014}. Coordinating the array of necessary hardware into a coherent experimental design---with the millisecond precision required to study the brain---can be daunting.

Historically, researchers have developed software to automate behavior experiments as-needed within their lab or relied on purchasing proprietary software (eg. \citep{elliottNationalInstrumentsLabVIEW2007}). Open-source alternatives have emerged recently, often developed in tandem with hardware peripherals available for purchase \citep{ephysPyControl2019,sandersSanworksBPod}. However, the diverse hardware and software requirements for behavioral experiments often lead researchers to cobble together multiple tools to perform even moderately complex experiments. Indeed, most software packages do not attempt to simultaneously support custom hardware operation, behavioral task logic, stimulus generation, and data acquisition. Idiosyncratic systems can hinder reproducibility, especially if the level of detail reported in a methods section is sparse\citep{wallReliabilityStartsExperimental2019}. Additionally, development time and proprietary software are expensive, as are the custom hardware peripherals that are required to use most available open-source behavior software.
\vspace{12pt}

Here we present Autopilot, a complete open-source software and hardware framework for behavioral experiments. We leverage the power of distributed computing using the surprisingly capable Raspberry Pi 4\sidenote{See Table \ref{hwtab}} to allow researchers to coordinate arbitrary numbers of heterogeneous hardware components in arbitrary experimental designs.

Autopilot takes a different approach than existing systems to overcome the technical challenges of behavioral research: \textit{just use more computers}. Specifically, the advent of inexpensive single-board computers (ie. the Raspberry Pi) that are powerful enough to run a full Linux operating system allows a unified platform to run on every Pi or other computer in the system so that they can work together seamlessly. At the core of its architecture is a networking protocol (Section \ref{sec:networking}) that is fast enough to stream electrophysiological or imaging data and flexible enough to make the mutual coordination of hardware straightforward. 

This distributed design also makes Autopilot extremely scalable, as the Raspberry Pi's \$35 price tag makes it an order of magnitude less costly than comparable systems (Section \ref{sec:expense}). Its low cost doesn't come at the expense of performance or useability: Autopilot also has an order of magnitude greater measurement precision and an order of magnitude lower latency than comparable systems (Sections \ref{sec:lowlevel} and \ref{sec:tests}).

Autopilot balances experimental flexibility with support. Its task design infrastructure is flexible enough to perform arbitrary experiments, but also provides support for data management, plotting task progress, and custom training regimens. We provide a set of modular tools for users to easily build common tasks (such as the two-alternative forced choice task described in Section \ref{sec:tasks}), and have also written complete low-level API documentation to facilitate any tinkering needed to make Autopilot do whatever is needed. Rather than relying on costly proprietary hardware modules, users can take advantage of the wide array of peripherals and extensive community support available for the Raspberry Pi. 

Finally, we have designed Autopilot to do reproducible research. Experiments are not written as scripts that are reliant on the particularities of each researcher's hardware configuration. Instead, we have designed the system to encourage users to write reusable, portable experiments that are incorporated into a public central library. Every parameter that defines an experiment is automatically saved in  publication-ready format, removing ambiguity in reported methods and facilitating exact replication with a single file.

\vspace{12pt}

We\marginnote{We would like to acknowledge and thank Lucas Ott for doing much of the behavioral training, Brynna Paros and Nick Sattler for their help with constructing our behavioral boxes, Matt Smear and Reese Findley for loaning us their Bpod for far longer than they intended to, Erik Flister whose Ratrix software inspired some of the design features of Autopilot \citep{meierCollinearFeaturesImpair2011}, several artists on \url{flaticon.com} (\href{https://www.flaticon.com/authors/freepik}{Freepik}, \href{https://www.flaticon.com/authors/nikita-golubev}{Nikita Golubev}, \href{https://www.flaticon.com/authors/those-icons}{Those Icons}) whose work served as stems for many of the figures, and the Janet Smith House for the endless support and relentless criticism of the figures. This material is based on work supported by NIH NIDCD R01 DC-015828, NSF Graduate Research Fellowship No. 1309047, and a University of Oregon Incubating Interdisciplinary Initiatives award.} begin by defining the requirements of a complete behavioral system and evaluating two current examples (Sections \ref{sec:existing} and \ref{sec:limitations}). We then describe Autopilot's design principles (Section \ref{sec:design}) and how they are implemented in the program's structure (Section \ref{sec:structure}). We close with a demonstration of its current capabilities and our plans to expand them (Sections \ref{sec:tests} and \ref{sec:future}).

\clearpage

\section{Existing Systems for Behavioral Experiments}
\label{sec:existing}

A complete system to automate behavioral experiments has 6 requirements:

\begin{enumerate}

\item \hyperref[sec:hardware]{Hardware}\marginnote{} to interact with the experimental subject, including \textbf{sensors} (eg. photodiodes, cameras, rotary encoders) to receive input and \textbf{actuators} (eg. lights, motors, solenoids) to provide feedback.
\item Some\marginnote{} capability to synthesize and present sensory \hyperref[sec:stim]{stimuli}. Ideally both discrete stimuli, like individual tone pips or grating patches, and continuous stimuli, like those used in virtual reality experiments, should be possible.
\item A \marginnote{} framework to coordinate hardware and stimuli as a \hyperref[sec:tasks]{task}. Task definition should be flexible such that it facilitates rather than constrains experimental design.
\item A \hyperref[sec:data]{data management}\marginnote{} system that allows fine control of data collection and format. Data should be human readable and include complete metadata that allows independent analysis and reproduction.
\item Some\marginnote{} means of \hyperref[sec:plotting]{visualizing data} as it is collected in order to  observe task status. It should be possible to customize visualization to the needs and structure of the task.
\item Finally,\marginnote{} a \hyperref[sec:ui]{user interface} to control task operation. The UI should make it possible for someone who does not program to operate the system.
\end{enumerate}

We\marginnote[-0.6cm]{} will briefly describe two other systems that are "complete" as described above: pyControl and Bpod.

%\vspace{16pt}
%\sffamily{\textbf{\Large{pyControl}}}\normalfont
\subsection{pyControl}

\href{https://pycontrol.readthedocs.io/en/latest/}{pyControl}\marginnote[0cm]{} is a behavioral framework built in Python by the Champalimaud Foundation. It uses the \href{https://micropython.org/}{micropython microcontroller} ("pyboard") as its primary hardware device along with several extension boards \href{http://www.open-ephys.org/store/pycontrol}{sold by openephys}. The pyboard has four I/O ports, or eight with a multiplexing expander board. Schematics are available for many other hardware components like solenoid valve drivers and rotary encoders. Multiple pyboards can be connected to a computer via USB and run independent tasks simultaneously with a GUI.

There is limited support for some parametrically defined sound stimuli, presented from a separate amplifier connected using the I2C protocol. Visual stimuli are unsupported.

Like most behavioral software, pyControl uses a finite-state machine formalism to define its tasks. A task is a set of discrete states, each of which has a set of events that transition the task from one state to another. pyControl also allows timed transitions between states, and one function that is called on every event for a rough sort of parallelism.

\begin{marginfigure}[-0.4cm]
\begin{minted}[frame=lines,fontsize=\small]{python}
D 0 2
D 8976 3
D 8976 1
P 8976 Print Statement
D 10162 3
D 10163 2
\end{minted}
\caption{pyControl data is stored as plain text, each line having a type (\textbf{D}ata or \textbf{P}rint), timestamp, and state}
\label{fig:pycdata}
\end{marginfigure}

The facility for data management is limited. All events and states are stored alongside timestamps as a plain text log file, one file per subject per session (Figure \ref{fig:pycdata}).

There is only one plot type available in the GUI, a raster plot of events, and no facility for varying the plot by task type. The GUI is otherwise quite capable, including the ability to batch run subjects, redefine task variables, and configure hardware.\\

%\sffamily{\textbf{\Large{Bpod}}}\normalfont
\subsection{Bpod}

Bpod\marginnote{} is primarily a collection of hardware designs and an assembly service run by \href{https://www.sanworks.io/about/about.php}{Sanworks LLC.} Similar to pyControl, each Bpod behavior box is based on a finite-state machine microcontroller with four I/O ports. Additional hardware modules provide extended functionality.

The software that runs Bpod is a \href{https://sites.google.com/site/bpoddocumentation/bpod-user-guide/function-reference-beta}{sparsely documented} MATLAB package. A task is implemented as a MATLAB script that constructs a new state machine for each trial, uploads it to the Bpod, and waits for the trial to finish. As a result, only one Bpod can be used per host computer, or at least per MATLAB session. Data are stored as trial-split events in a MATLAB structure.

There are a few basic plots for two-alternative forced choice tasks, but any plotting is done in the main loop so the MATLAB graphics engine blocks the program between trials. Bpod has a reasonably complete GUI for managing the hardware and running tasks, but it is error-prone and highly technical (Figure \ref{fig:bpodgui}).

\begin{marginfigure}
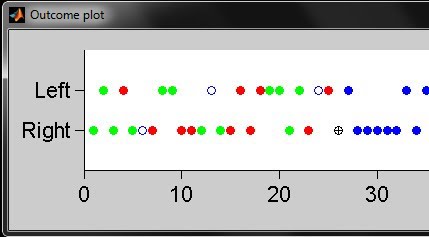
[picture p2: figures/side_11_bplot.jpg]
\noindent
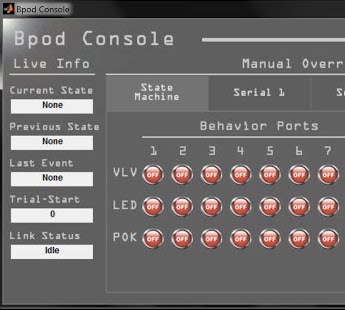
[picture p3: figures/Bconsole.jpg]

\caption{A Bpod event plot (above) showing the results of individual behavioral trials, and the Bpod GUI (below).} 
\label{fig:bpodgui}
\end{marginfigure}

\vspace{16pt}

For brevity we have omitted many other excellent tools that perform some subset of the operations of a complete behavioral system.\sidenote[][1cm]{\textbf{Other tools:}\\
- Expyriment\citep{krauseExpyrimentPythonLibrary2014} - \href{https://www.expyriment.org/}{site}, \href{https://github.com/expyriment/expyriment.git}{git}\\
- PsychoPy\citep{peircePsychoPy2ExperimentsBehavior2019} - \href{https://www.psychopy.org/}{site}, \href{https://github.com/psychopy/psychopy}{git}\\
- OpenSesame\citep{mathotOpenSesameOpensourceGraphical2012} - \href{https://osdoc.cogsci.nl/}{site}, \href{https://github.com/smathot/OpenSesame}{git}\\
- SMiLE - \href{https://smile-docs.readthedocs.io/en/latest/}{docs}\\
- ArControl\citep{chenArControlArduinoBasedComprehensive2017} - \href{https://github.com/chenxinfeng4/ArControl}{git}\\
- and see \href{http://openbehavior.com/}{OpenBehavior}
}

\section{Limitations of Existing Systems}
\label{sec:limitations}

We see several limitations with these and other behavioral systems:

\begin{itemize}[after=\vspace{-\topsep}]
    \item \textbf{Hardware} - Both Pycontrol and Bpod strongly encourage users to purchase a limited set of hardware modules and add-ons from their particular hardware ecosystem. If a required part is not available for purchase, neither system provides a clear means of interacting with custom hardware, requiring the user to 'tack on' loosely-integrated components---we found \href{https://github.com/erlichlab/BpodSoundModule}{one such lab} using a Raspberry Pi to deliver sounds in their Bpod task.   There is also a hard limit on the \textit{number} of hardware peripherals that can be used in any given task, as there is no ability to use additional pyboards or Bpod state machines. The microcontrollers used in these systems also impose strong limits on their software: neither run a full, high-level programming language\sidenote{Bpod runs \href{https://github.com/sanworks/Bpod_StateMachine_Firmware}{custom firmware} written in C++ on a \href{https://www.pjrc.com/store/teensy36.html}{Teensy 3.6} microcontroller. pyControl's pyboard implements \href{https://micropython.org/}{micropython}, a subset of Python that excludes canonical libraries like numpy\citep{waltNumPyArrayStructure2011} or scipy\citep{jonesSciPyOpenSource2001}}. We will discuss this further in \hyperref[sec:singlelanguage]{section \ref*{sec:singlelanguage}}. A broader  limitation of existing systems is the difficulty of flexibly integrating the diverse hardware and analytical tools necessary to perform the next generation of behavioral neuroscience experiments that study "naturalistic, unrestrained, and minimally shaped behavior"\citep{dattaComputationalNeuroethologyCall2019}.
    \item \textbf{Stimuli} - Stimuli are not tightly integrated into either of these systems, requiring the user to write custom routines for their synthesis, presentation, and description in the resulting data. Neither are capable of delivering visual stimuli. Bpod only supports raw audio waveforms presented with either a proprietary analog output hardware module or using PsychToolbox from the host computer. Some parametric audio stimuli are included in the \href{https://bitbucket.org/takam/pycontrol/src/default/pyControl/audio.py}{pyControl source code} but we were unable to find any documentation or examples of their use. %
\end{itemize}\nobreak%
\begin{marginfigure}[0.35cm]
\begin{minted}[frame=lines,fontsize=\small]{matlab}
for currentTrial = 1:MaxTrials
% new state matrix every trial
sma = NewStateMatrix();

% add states and transitions
sma = AddState(sma, 
    'Name', 'Wait', ...
    'Timer', 0,...
    'StateChangeConditions', ...
    {'Port2In', 'Delay'}, ...
    'OutputActions', ...
    {'AudioPlayer1','*'});
% add more states...

% upload and run task
SendStateMatrix(sma);
RawEvents = RunStateMatrix;

% manually gather data and params
BpodSystem.Data = AddTrialEvents(
    BpodSystem.Data, RawEvents);
    
% plotting in the main loop
UpdateSideOutcomePlot(...);
UpdateTotalRewardDisplay(...);

% manually save data
SaveBpodSessionData;
end
\end{minted}
\caption{\href{https://github.com/sanworks/Bpod_Gen2/blob/master/Examples/Protocols/AnalogSound2AFC/AnalogSound2AFC.m}{Bpod's general task structure.}}
\label{fig:bpodtask}
\end{marginfigure}\nobreak
\begin{itemize}[resume*, before=\vspace{0pt}, after=\vspace{\baselineskip}]%
    \item \textbf{Tasks} - Tasks in both systems require a large amount of code and effort duplication. Neither system has a notion of reusable tasks or task 'templates,' so every user needs to rewrite every task from scratch. Bpod's structure in particular tends to encourage users to write long \href{https://github.com/sanworks/Bpod_Gen2/blob/master/Examples/Protocols/AnalogSound2AFC/AnalogSound2AFC.m}{task scripts} that are difficult to read (Figure \ref{fig:bpodtask}) because much of its codebase is 'backend' code for compiling and communicating with the state machine, so users have to write basic routines like stimulus creation themselves. Another factor that contributes to the difficulty of task design in these systems is the need to work around the limitations of finite state machines, which we discuss further in section \ref{sec:fsmlimits}.
    \item \textbf{Data} - Data storage and formatting is basic, requiring extensive additional processing to make it human readable. For example, to determine whether a subject got a trial correct in an \href{https://github.com/sanworks/Bpod_Gen2/blob/master/Examples/Protocols/Light/Light2AFC/Light2AFC.m}{example} Bpod experiment, one would use the following code:
    
    \mintinline{matlab}{SessionData.RawEvents.Trial{1,1}.States.Punish(1) ~= NaN}
    
    As a result, data format is idiosyncratic to each user, making data sharing dependent on manual annotation and metadata curation from investigators. Additionally, since the parameters of experiments are not saved by default---and the GUIs of both systems allow parameters to be changed at will---critical data could be lost and experiments could be made unreproducible unless the user writes custom code to save them.
    \clearpage
    \item \textbf{Visualization \& GUI} - The GUIs of each of these systems are highly technical, and are not designed to be easily used by non-programmers. Visualization of task progress is quite rigid in both systems, either a timeseries of task states or plots specific to two-alternative forced choice tasks. There is no obvious way to adapt plots to specific tasks.
\end{itemize}

In short, existing systems for behavioral experiments are limited by the hardware they can use, the tasks they can implement, and the ease with which they can be implemented. Some of these limitations are cosmetic---fixable with additional code or hardware---but several of the most crucial are intrinsic to the design of these systems.

These systems, among others, have pioneered the development of modern behavioral hardware and software, and are to be commended for being open-source and highly functional. One need look no further for evidence of their usefulness than to their adoption by many labs worldwide. At the time that these systems were developed, a general-purpose single-board computer with performance like the Raspberry Pi 4 was not widely available. The above two systems are not unique in their limitations, but are reflective of broader constraints of developing experimental tools. We are only able to articulate the design principles that differentiate Autopilot by building on their work. 

\chapter{Design}
\label{sec:design}

\newthought{Autopilot distributes experiments} across a network of Raspberry Pis,\sidenote{\href{https://www.raspberrypi.org/products/raspberry-pi-4-model-b/}{Raspberry Pi model 4B}, see \hyperref[hwtab]{Table \ref*{hwtab}}} a type of inexpensive single-board computer. 

\vspace{12pt}

\textbf{Autopilot has three primary design principles:}

\begin{enumerate}
    \item \hyperref[sec:efficiency]{\textbf{Efficiency}} - Autopilot should minimize computational overhead and maximize use of hardware resources.
    \item \hyperref[sec:flexibility]{\textbf{Flexibility}} - Autopilot should be transparent in all its operations so that users can expand it to fit their use-case.
    \item \hyperref[sec:reproducibility]{\textbf{Reproducibility}} - Autopilot should maximize standardization and minimize the potential for the black-box of local reprogramming. Autopilot should maximize the information it stores about its operation as part of normal data collection.
\end{enumerate}

\section{Efficiency}
\label{sec:efficiency}

Though it is a single board, the Raspberry Pi operates more like a computer than an integrated circuit. It most commonly runs a custom Linux distribution, Raspbian, allowing Autopilot to use Python across the whole system. Using an interpreted language like Python running on Linux has inherent performance drawbacks compared to compiled languages running on embedded microprocessors. While Python's overhead is negligible on modern processors, Autopilot is nevertheless designed to maximize computational efficiency.

\subsection{Concurrency}

\begin{marginfigure}[3.5cm]

\caption{A single-threaded program executes all operations sequentially, using a single process and cpu core.}
\label{fig:singlethread}
\end{marginfigure}

Most behavioral software is single-threaded (Figure \ref{fig:singlethread}), meaning the program will only perform a single operation at a time. If the program is busy or waiting for an input, other operations are blocked until it is finished.

Autopilot distributes computation across multiple processes and threads to take advantage of the Raspberry Pi's four CPU cores. Every object in Autopilot does its work in separate \textbf{threads}. Specifically, Autopilot spawns separate threads to process messages and events, an architecture described more fully in \hyperref[sec:networking]{section \ref*{sec:networking}}. Threading does not offer true concurrency\sidenote{See David Beazley's  \href{http://www.dabeaz.com/python/UnderstandingGIL.pdf}{'Understanding the Global Interpreter Lock'} and associated \href{http://www.dabeaz.com/GIL/gilvis/index.html}{visualizations}.}, but does allow Python to distribute computational time between operations so that, for example, waiting for an event does not block the rest of the program, and events are not missed because the program is busy (Figure \ref{fig:multithread}).

\begin{marginfigure}

\caption{A multi-threaded program divides computation time of a single process and cpu core across multiple operations so that, for example, waiting for input doesn't block other operations.}
\label{fig:multithread}
\end{marginfigure}

Critical operations that are computationally intensive or cannot be interrupted are given their own dedicated \textbf{processes}. Linux allows individual cores of a processor to be reserved for single processes, so individual Raspberry Pis are capable of running four truly parallel processing streams. For example, all Raspberry Pis in an Autopilot swarm create a messaging client to handle communication between devices which runs on its own processor core so no messages are missed. Similarly, if an experiment requires sound delivery, a realtime \hyperref[sec:stim]{sound engine} in a separate process (Figure \ref{fig:multiprocess}) also runs on its own core.

\begin{marginfigure}[0.1cm]
 
 \caption{A multi-process program is truly concurrent, allowing multiple cpu cores to operate in parallel.}
 \label{fig:multiprocess}
\end{marginfigure}

\subsection{Leveraging Low-Level Libraries}
\label{sec:lowlevel}

Autopilot uses Python as a "glue" language, where it wraps and coordinates faster low-level compiled code\citep{vanrossumGlueItAll1998}.  
Performance-critical components of Autopilot are thin wrappers around fast C libraries (Table \ref{tab:libraries}).

\begin{margintable}[0.1cm]
\caption{A few libraries Autopilot uses}
\label{tab:libraries}
\noindent\begin{tabularx}{\linewidth}{Rl}
\toprule
 \textbf{\href{http://jackaudio.org/}{jack}} & realtime audio \\
 \textbf{\href{http://abyz.me.uk/rpi/pigpio/index.html}{pigpio}} & GPIO control \\
 \textbf{\href{http://zeromq.org/}{ZeroMQ}} & networking \\
 \textbf{\href{https://www.qt.io/}{Qt}} & GUI \\
 \bottomrule
\end{tabularx}

\end{margintable}

Since Autopilot coordinates its low-level components in parallel rather putting everything inside one "main loop," Autopilot actually has \textit{better} temporal resolution than  single-threaded systems like Bpod or pyControl, despite the realtime nature of their dedicated processors (Table \ref{tab:precision}).

\begin{margintable}
\caption{Using pigpio as a dedicated I/O process gives autopilot greater measurement precision}
\label{tab:precision}
\noindent\begin{tabularx}{\linewidth}{rR}\toprule
& Precision \\
\midrule
Autopilot (\href{http://abyz.me.uk/rpi/pigpio/pigpiod.html}{pigpio}) & $5\mu s$ \\
\href{https://github.com/sanworks/Bpod_StateMachine_Firmware/blob/059d1e9195f5bb7d0d5cd7b33f56342eb5a3a55c/Dev/StateMachineFirmware/StateMachineFirmware.ino\#L196}{Bpod} & $100\mu s$ \\
\href{https://bitbucket.org/takam/pycontrol/src/c678552ac57be2108a5461e0c5f8051ce7d3816a/pyControl/framework.py?at=default\&fileviewer=file-view-default\#framework.py-278}{pyControl} & $1000\mu s$ \\
\bottomrule
\end{tabularx}

\end{margintable}

\subsection{Caching}

Finite-state machines are only aware of the current state and the events that transition it to future states. They are thus incapable of exploiting the often predictable structure of behavioral tasks to precompute future states and precache stimuli. Further, to change task parameters between trials (eg. changing the rewarded side in a two-alternative forced-choice task), state machines need to be fully reconstructed and reuploaded to the device that runs them each time.

Autopilot precomputes and caches as much as possible. Rather than wait "inside" a state, Autopilot prepares each of the next possible events and saves them for immediate execution when the appropriate trigger is received. Static stimuli are prepared once at the beginning of a behavioral session and stored in memory. Before their presentation, they are buffered to minimize latency.

\vspace{16pt}

Autopilot's efficient design lets it access the best of both worlds---the speed and responsiveness of compiled code on dedicated microprocessors and the accessibility and flexibility of interpreted code.

\clearpage

\section{Flexibility}
\label{sec:flexibility}

\subsection{Single-language}
\label{sec:singlelanguage}

Behavior software that uses dedicated microprocessors like Bpod must have some routine for compiling the high-level abstraction of the experiment into machine code. This gives those systems a theoretical advantage in processing speed, but the compiler becomes the bottleneck of complexity: only those things that can be compiled can be included in the experiment. This may in part contribute to the ubiquity of state-machine formalisms in behavior software.

Because Python is used throughout the system, extending Autopilot's functionality is straightforward. Task design (see section \hyperref[sec:tasks]{\ref*{sec:tasks}}) is effectively arbitrary---anything that can be expressed in Python is a valid task. Hardware can also be implemented arbitrarily, including hardware that makes use of external libraries (eg. ACQ4\citep{campagnolaACQ4OpensourceSoftware2014} and our \hyperref[item:othertools]{planned} integration with OpenEphys).

\subsection{Modularity}

Although Autopilot deeply integrates with the Raspberry Pi's hardware, we have also worked to make its components modular. Modularity has 3 primary advantages:
\begin{enumerate}
    \item \textbf{Modularity} \marginnote{}\textbf{makes code more flexible} by reducing the constraints imposed by unstructured code interdependencies
    \item \textbf{Modularity} \marginnote{}\textbf{makes code more intelligible} by logically distributing tasks to discrete classes
    \item \textbf{Modularity} \marginnote{}\textbf{reduces effort-duplication} by allowing multiple, similar classes to be created with inheritance rather than copying and pasting.
\end{enumerate}

There is no such thing as "incompatible hardware" with Autopilot because the classes that control hardware are independent from the code that provides other core functionality. In systems without modular design, hardware implementation is spread across the codebase; for example to add a new type of hardware output to a Bpod system, one would need to write \href{https://github.com/sanworks/Bpod_Gen2/blob/master/FIRMWARE\%20README.txt}{new firmware for it in C}, \href{https://github.com/sanworks/Bpod_StateMachine_Firmware/blob/v22/Preconfigured/StateMachine-Bpod2_0/StateMachine-Bpod2_0.ino}{modify Bpod's existing firmware}, hunt through the code to modify how \href{https://github.com/sanworks/Bpod_Gen2/blob/71f3a256b68926b65eae71e10fd747bd28e7ba7d/Functions/State\%20Machine\%20Assembler/AddState.m#L170}{states are added} and \href{https://github.com/sanworks/Bpod_Gen2/blob/71f3a256b68926b65eae71e10fd747bd28e7ba7d/Functions/\%40BpodObject/SetupStateMachine.m#L123}{state machines are assembled}, add its controls explicitly \href{https://github.com/sanworks/Bpod_Gen2/blob/71f3a256b68926b65eae71e10fd747bd28e7ba7d/Functions/Override\%20Panels/StateMachinePanel_2_0_0.m}{to the GUI}, and so on. 

Tasks specify what type of hardware is needed to run them, but are agnostic about the way the hardware is implemented, making their descriptions more portable. Tasks that have the same structure but differ in hardware (eg. a freely moving two-alternative forced choice task in which a mouse visits several IR sensors, or a head-fixed two-alternative forced choice task in which a mouse runs on a wheel to indicate its choice) can be implemented by a trivial subclass that modifies  the hardware description rather than completely rewriting the task.

\subsection{Structured Expansion \& Code Transparency}
\label{sec:expansion}

We call Autopilot a software framework because in addition to providing classes and methods to run experiments out of the box, it also provides explicit structure that scaffolds any additional code that is needed by the user. Our goal is to clearly articulate in the documentation how modules should interact so that anyone can write code that works on any apparatus. 

Autopilot is designed for users with a range of programming expertise, from those who only want to interact with a GUI, to those who wish to fundamentally rewrite core operations for their particular experiment. As such, it is extensively documented: this paper provides a high-level introduction to its design and structure, its user guide describes how to use the program and provides examples, and its API-level documentation describes in granular detail how the program actually works\sidenote{The user guide and API documentation are available at \url{docs.auto-pi-lot.com}}. Nothing is "off-limits" to the user---there isn't any hidden, undocumented hardware code behind the curtain. We want users to be able to understand how and why everything works the way it does so that Autopilot can be adapted and expanded to any use-case.

A broader goal of Autopilot is to build a library of flexible task prototypes that can be tweaked and adapted, hopefully reducing the number of times the wheel is reinvented. We have attempted to nudge users to write reusable tasks by designing Autopilot such that rather than writing separate task scripts that are loaded and run by the program, tasks are written into a fork\sidenote{Autopilot is version controlled using \href{https://git-scm.com/}{git}. Users develop tasks in a copy, or 'fork' of the library that keeps track of their changes so that they can later be re-integrated, or 'pulled', into the main library.} of the library itself. When publishing research that uses a particular task, users are incentivized to pull the changes they have made in their fork back into the central library because doing so makes that task available to anyone using Autopilot. Autopilot's documentation is automatically generated from structured comments\sidenote{using \href{http://www.sphinx-doc.org/en/master/}{Sphinx}}, which naturally establishes a minimal level of documentation that we will require to have a task accepted into the main library. We hope the combination of these design nudges and explicit development instructions in the user guide encourages users to make contributing well-documented, reusable tasks a normal part of using Autopilot.

\subsection{Message Handling}

Modular software needs a well-defined protocol to communicate between modules, and Autopilot's is heavily influenced by the concurrency philosophy\sidenote{"ZeroMQ [...] has a subversive effect on how you develop network-capable applications. [...] message processing rapidly becomes the central loop, and your application soon breaks down into a set of message processing tasks."\\"If there's one lesson we've learned from 30+ years of concurrent programming, it is: \textit{just don't share state.}"\\\vspace{6pt}\hspace*{\fill} -\href{http://zguide.zeromq.org/}{The ZeroMQ Guide}} of ZeroMQ\citep{hintjensZeroMQMessagingMany2013}. All communication between computers and modules happens with ZeroMQ messages, and handling those messages is the main way that Autopilot handles events. A key design principle is that Autopilot components should not "share state"---they can communicate, but they are not \textit{dependent} on one another. While this may seem like a trivial detail, having networking and message-handling at its core has three advantages that make Autopilot a fundamental departure from previous behavioral software.

First, new software modules can be added to any system by simply dropping in a standalone networking object. There is no need to dramatically reorganize existing code to make room for new functionality. Instead new modules can receive, process, and send information by just connecting to a parent module in the swarm. For example, each \hyperref[sec:plotting]{plot} opens a network connection to stream incoming task data independently from the stream that is saving the data.

Second, Autopilot can be made to interact with other software libraries that use ZeroMQ. For example, The OpenEphys GUI for electrophysiology \href{https://open-ephys.atlassian.net/wiki/spaces/OEW/pages/23265310/Network+Events}{can send and receive ZMQ messages} to execute actions such as starting or stopping recordings. Interaction with other software is also useful in the case that some expensive computation needs to happen mid-task. For example, one could send frames captured from a video camera on a Raspberry Pi to a GPU computing cluster for tracking the position of the animal. Since ZeroMQ messages are just TCP packets it is also possible to communicate over the internet for remote control or to communicate with a data server.

Third, making every component network-capable allows tasks to be distributed over multiple Raspberry Pis. Chaining multiple Pis distributes the computational load, allowing, for example, one Raspberry Pi to record and process video while another runs a sound server and delivers rewards. Autopilot expands with the complexity of your task, simultaneously eliminating limitations on quantity of hardware peripherals while ensuring latency is minimal. More interestingly, distributing tasks allows the arbitrary construction of what we call "behavioral topologies," which we describe in \hyperref[sec:topology]{section \ref*{sec:topology}}.

\clearpage

\section{Reproducibility}
\label{sec:reproducibility}

\subsection{Standardized task descriptions}

\begin{marginfigure}[1.75cm]

\caption{\textbf{"Minor" details have major effects.} Proportion of mice (each point, n=4) that were successful learning the first stage of the speech task described in \citep{saundersMiceCanLearn2019} across 10 behavior boxes with variable reward sizes. A $2 \mu L$ difference in reward size had a surprisingly large effect on success rate.}
\label{fig:calibration}
\end{marginfigure}

The implementation and fine details of a behavioral experiment matter. Seemingly trivial details like milliseconds of delay between trial phases and microliters of reward volume can be the difference between a successful and unsuccessful task (Figure \ref{fig:calibration}). \textit{Reporting} those details can thus be the difference between a reproducible and unreproducible result.  Researchers also often use "auxiliary" logic in tasks---such as methods for correcting response bias---that are never completely neutral to the interpretation of results. These too can be easily omitted due to brevity or memory in plain-English descriptions of a task, such as those found in Methods sections. Even if all details of an experiment were faithfully reported, the balkanization of behavioral software into systems peculiar to each lab (or even to individuals within a lab) makes actually performing a replication of a behavior result expensive and technically challenging. Widespread use of experimental tools that are not explicitly designed to preserve every detail of their operation presents a formidable barrier to rigorous and reproducible science\citep{wallReliabilityStartsExperimental2019}.

%
\begin{marginfigure}[1.1cm]
\begin{minted}[frame=lines,fontsize=\small]{json}
{
"step_name"    : "tone_discrim",
"task_type"    : "2AFC",
"bias_mode"    : 0,
"punish_sound" : false,
"stim" : {
  "sounds" : {
    "L": {
      "duration"  : 100,
      "frequency" : 10000,
      "type"      : "tone",
      "amplitude" : 0.01},
    "R": {"...":"..."}}},
"reward": {
  "type"     : "volume",
  "volume"   : 20},
"graduation" : {
    "type"      : "accuracy",
    "threshold" : 0.75,
    "window"    : 400},
}
\end{minted}
\caption{Task parameters are stored as portable JSON, formatting has been abbreviated for clarity.}
\label{fig:params}
\end{marginfigure}%
%
%
Autopilot splits experiments into a) the \textbf{code} that runs the experiment, which is intended to be standardized and shared across implementations, and b) the \textbf{parameters} (Figure \ref{fig:params}) that define your particular experiment. For example, two-alternative forced choice tasks have a shared structure regardless of the stimulus modality, but only your task plays pitch-shifted national anthems. Critically, this division of labor enables the possibility of developing a shared library of tasks as described in \hyperref[sec:expansion]{section \ref{sec:expansion}}%

The practice of reporting exactly the parameter description used by the software to run the experiment removes any chance for incompleteness in reporting. Because all task parameters are included in the produced data files, tasks are fully portable and can be reimplemented exactly by anyone that has comparable hardware to yours. 

\subsection{Self-Documenting Data}
\label{sec:data}

A major goal of the open science movement is to normalize publishing well-documented and clearly-formatted data alongside every paper. Typically, data are acquired and stored in formats that are lab-idiosyncratic or ad-hoc. Making data publishable then requires a laborious cleaning process. In the worst-case scenario, this cleaning process unearths some critically missing information about the experiment, requiring awkward caveats in the Methods section. Moreover, without careful version control, any changes made to the task code or parameters can be lost, making it difficult to compare last week's data to last month's.

\begin{marginfigure}[0.5cm]

\caption{Example data structure. All information necessary to reconstruct an experiment is automatically stored in a human-readable HDF5 file.}
\label{fig:datastx}
\end{marginfigure}

The best way to make data publishable is to avoid cleaning data altogether and \textit{design good data hygiene practices into the data acquisition process.} Autopilot automatically stores all the information required to fully reconstruct an experiment, including any changes in task parameters or code version that happen throughout training as the task is refined.

Autopilot data is stored in \href{https://support.hdfgroup.org/HDF5/whatishdf5.html}{HDF5} files, a hierarchical, high-performance file format. HDF5 files support metadata throughout the file hierarchy, allowing annotations to natively accompany data. Because HDF5 files can store nearly all commonly used data types, data from all collection modalities---trialwise behavioral data, continuous electrophysiological data, imaging data, etc.---can be stored together from the time of its acquisition. Data is always stored with the conditions of its collection, and is ready to analyze and publish immediately (Figure \ref{fig:datastx}). No Autopilot-specific scripts are needed to import data into your analysis tool of choice---anything that can read HDF5 files can read Autopilot data. 

In future versions we will implement the Neurodata Without Borders standard\citep{rubelNWBAccessibleData2019}, further enabling Autopilot data to be immediately incorporated into existing processing pipelines (see section \ref{sec:future}).

\subsection{Expense}
\label{sec:expense}

\begin{marginfigure}[2.6cm]

\caption{When comparing a value across groups, eg. a genetic knockout vs. wildtype, even a modest intra-animal (or, more generally, intra-cluster) correlation (ICC) causes the false positive rate to be far above the nominal $\alpha = 0.05$. Shown are false positive rates for simulated data with various numbers of "cells" recorded for comparisons between two groups of 5 animals each with a real effect size of 0. We note that 741 simultaneously recorded cells were reported in \citep{junFullyIntegratedSilicon2017} and a mean ICC of 0.19 across 18 neuroscientific datasets was reported in \citep{aartsSolutionDependencyUsing2014}}
\label{fig:icc}
\end{marginfigure}

Autopilot is an order of magnitude less expensive than comparable behavioral systems (Table \ref{tab:cost}). We think the expense of a system is important for two reasons: scientific equity and statistical power. 

The distribution of scientific funding is highly skewed, with a large proportion of research funding concentrated in relatively few labs\citep{katzBiomedicalEliteInequality2017}. Lower research costs benefit all scientists, but lower instrumentation costs directly increase the accessibility of state-of-the-art experiments to labs with less funding. Since well-funded labs also tend to be concentrated at a few (well-funded) institutions, lower research costs also broaden the base of scientists outside traditional research institutions that can stay at the cutting edge\citep{ashkenasEvenAffirmativeAction2017,clausetSystematicInequalityHierarchy2015,pearceExpandingEquitableAccess2019}.

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

Although the expense of multi-photon imaging and high-density electrophysiology will always impose an experimental bottleneck, behavioral training time is often the greater determinant of study sample size. Typical behavioral experiments require daily training sessions often carried out over weeks and months, while far fewer imaging or electrophysiology sessions are carried out per animal.  Training large cohorts of animals in parallel is thus the necessary basis of a well-powered imaging or electrophysiology experiment.

\begin{table}
\caption{\textbf{Cost for Basic 2AFC System}\\
\noindent"Nosepoke" includes a solenoid valve, IR sensor, water tube, LED, housing, and any necessary driver PCBs.}
\label{tab:cost}
\noindent\begin{tabularx}{\linewidth}{XRRR}\toprule
& Autopilot & pyControl & Bpod  \\
\midrule
Behavior CPU & \href{https://www.adafruit.com/product/3775?src=raspberrypi}{\texttt{\$35}} & \href{http://www.open-ephys.org/store/pycontrol}{\texttt{\$284}} & \href{https://sanworks.io/shop/viewproduct?productID=1024}{\texttt{\$745}}\\
Nosepoke (3x) & \texttt{\$216} & \href{http://www.open-ephys.org/store/pycontrol-peripherals}{\texttt{\$579}} & \href{https://sanworks.io/shop/viewproduct?productID=1009}{\texttt{\$735}} \\
\textbf{Total for One} & \textbf{\texttt{\$251}} & \textbf{\texttt{\$920}} & \textbf{\texttt{\$1480}}\\
\midrule
Five Systems & \texttt{\$1255} & \texttt{\$4600} & \texttt{\$7400} \\
Host CPU(s) & \texttt{\$1000} & \texttt{\$5000} & \texttt{\$5000} \\
\textbf{Total for Five} & \textbf{\texttt{\$2255}} & \textbf{\texttt{\$9600}} & \textbf{\texttt{\$12400}} \\
\midrule
\textbf{Total for Ten} & \textbf{\texttt{\$3510}} & \textbf{\texttt{\$19200}} & \textbf{\texttt{\$24800}} \\
\bottomrule
\end{tabularx}
\end{table}

\chapter{Program Structure}
\label{sec:structure}

\begin{figure*}

\caption{Overview of major Autopilot components}
\end{figure*}

\newthought{Autopilot consists of software and hardware modules} that are configured to create a behavioral \hyperref[sec:topology]{topology}. Independent \hyperref[sec:agents]{agents} linked by flexible \hyperref[sec:networking]{networking} objects fill different roles within a topology, such as hosting the \hyperref[sec:ui]{user interface}, controlling \hyperref[sec:hardware]{hardware}, or delivering \hyperref[sec:stim]{stimuli}. This infrastructure is ultimately organized to perform a behavioral \hyperref[sec:tasks]{task}.

\section{Tasks}
\label{sec:tasks}
\begin{marginfigure}[5.9cm]

\caption{Protocols consist of one or multiple tasks, tasks consist of one or multiple stages. Completion of all of a task's stages constitutes a trial, and meeting some graduation criterion like accuracy progresses a subject between tasks.}
\label{fig:taskstx}
\end{marginfigure}

Behavioral experiments in Autopilot are centered around \textbf{tasks}. Tasks are Python classes that describe the parameters, coordinate the hardware, and perform the logic of the experiment. Tasks may consist of one or multiple \textbf{stages}, completion of which constitutes a \textbf{trial} (Figure \ref{fig:taskstx}). Stages are analogous to states in the finite state machine formalism. 

Multiple tasks are combined to make \textbf{protocols}, in which animals move between tasks according to "graduation" criteria like accuracy or number of trials. Training an animal to perform a task typically requires some period of shaping where they are familiarized to the apparatus and the structure of the task. For example, to teach animals about the availability of water from "nosepoke" sensors, we typically begin with a "free water" task that simply gives them water for poking their nose in them. Having a structured protocol system prevents shaping from relying on intuition or ad hoc criteria.

\subsection{Task Components}
\label{sec:taskcomponents}

The following is a basic two-alternative choice (2AFC) task---a sound is played and an animal is rewarded for poking its nose in a designated target nosepoke. While simple, it is included here in full to show how one can program a task, including an explicit data and plotting structure, in roughly 60 lines of generously spaced Python.

\vspace{12pt}

Every task begins by describing four elements:
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

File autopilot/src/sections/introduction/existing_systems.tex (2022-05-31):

%!TEX root=../../autopilot.tex
\section{Existing Systems for Behavioral Experiments}
\label{sec:existing}

At minimum, a complete system to automate behavioral experiments has 6 requirements:

\begin{enumerate}

\item \hyperref[sec:hardware]{Hardware}\marginnote{} to interact with the experimental subject, including \textbf{sensors} (eg. photodiodes, cameras, rotary encoders) to receive input and \textbf{actuators} (eg. lights, motors, solenoids) to provide feedback.
\item Some\marginnote{} capability to synthesize and present sensory \hyperref[sec:stim]{stimuli}. Ideally both discrete stimuli, like individual tone pips or grating patches, and continuous stimuli, like those used in virtual reality experiments, should be possible.
\item A \marginnote{} framework to coordinate hardware and stimuli as a \hyperref[sec:tasks]{task}. Task definition should be flexible such that it facilitates rather than constrains experimental design.
\item A \hyperref[sec:data]{data management}\marginnote{} system that allows fine control of data collection and format. Data should be human readable and include complete metadata that allows independent analysis and reproduction. Ideally the program would also allow some means of realtime data processing of sensor values for use in a task.
\item Some\marginnote{} means of \hyperref[sec:plotting]{visualizing data} as it is collected in order to  observe task status. It should be possible to customize visualization to the needs and structure of the task.
\item Finally,\marginnote{} a \hyperref[sec:ui]{user interface} to control task operation. The UI should make it possible for someone who does not program to operate the system.
\end{enumerate}

We\marginnote[-0.6cm]{} will briefly describe two other systems that meet this definition of completeness: pyControl and Bpod.

%\vspace{16pt}
%\sffamily{\textbf{\Large{pyControl}}}\normalfont
\subsection{pyControl}

\href{https://pycontrol.readthedocs.io/en/latest/}{pyControl}\citep{akamOpensourcePythonbasedHardware2022}\marginnote[0cm]{} is a behavioral framework built in Python by the Champalimaud Foundation. It uses the \href{https://micropython.org/}{micropython microcontroller} ("pyboard") as its primary hardware device along with several extension boards \href{http://www.open-ephys.org/store/pycontrol}{sold by openephys}. The pyboard has four I/O ports, or eight with a multiplexing expander board. Schematics are available for many other hardware components like solenoid valve drivers and rotary encoders. Multiple pyboards can be connected to a computer via USB and run independent tasks simultaneously with a GUI.

There is limited support for some parametrically defined sound stimuli, presented from a separate amplifier connected using the I2C protocol. Visual stimuli are unsupported.

Like most behavioral software, pyControl uses a finite-state machine formalism to define its tasks. A task is a set of discrete states, each of which has a set of events that transition the task from one state to another. pyControl also allows timed transitions between states, and one function that is called on every event for a rough sort of parallelism. pyControl also allows the use of external variables to control state logic, making these state machines more flexible than strict finite state machines.

\begin{marginfigure}[-3.5cm]
\begin{minted}[frame=lines,fontsize=\small]{python}
D 0 2
D 8976 3
D 8976 1
P 8976 Print Statement
D 10162 3
D 10163 2
\end{minted}
\caption{pyControl data is stored as plain text, each line having a type (like \textbf{D}ata or \textbf{P}rint), timestamp, and state}
\label{fig:pycdata}
\end{marginfigure}

All events and states are stored alongside timestamps as a plain text log file, one file per subject per session (Figure \ref{fig:pycdata}). Analog data are stored in a custom binary serialization that alternates 4-byte data and timestamp integers.

There is only one plot type available in the GUI, a raster plot of events, and no facility for varying the plot by task type. The GUI is otherwise quite capable, including the ability to batch run subjects, redefine task variables, and configure hardware.\\

%\sffamily{\textbf{\Large{Bpod}}}\normalfont
\subsection{Bpod}
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

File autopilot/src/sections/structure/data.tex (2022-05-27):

%!TEX root=../../autopilot.tex
\section{Data}
\label{sec:datamodel}

As of v0.5.0, Autopilot uses \href{https://pydantic-docs.helpmanual.io/}{pydantic} to create explicitly typed and schematized data models. Submodules include \texttt{data} abstract \texttt{modeling} tools that define base model types like \texttt{Table}s, \texttt{Group}s, and sets of \texttt{Attributes}. These base modeling classes are then built into a few core data models like subject \texttt{Biography} information, \texttt{Protocol} declaration, and the \texttt{Subject} data model itself that combines them. Modeling classes then have multiple \texttt{interfaces} that can be used to create equivalent objects in other formats, like pytables for hdf5 storage, pandas dataframes for analysis, or exported to Neurodata Without Borders.
\clearpage
For example, consider a simplified version of the \texttt{Biography} model:
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

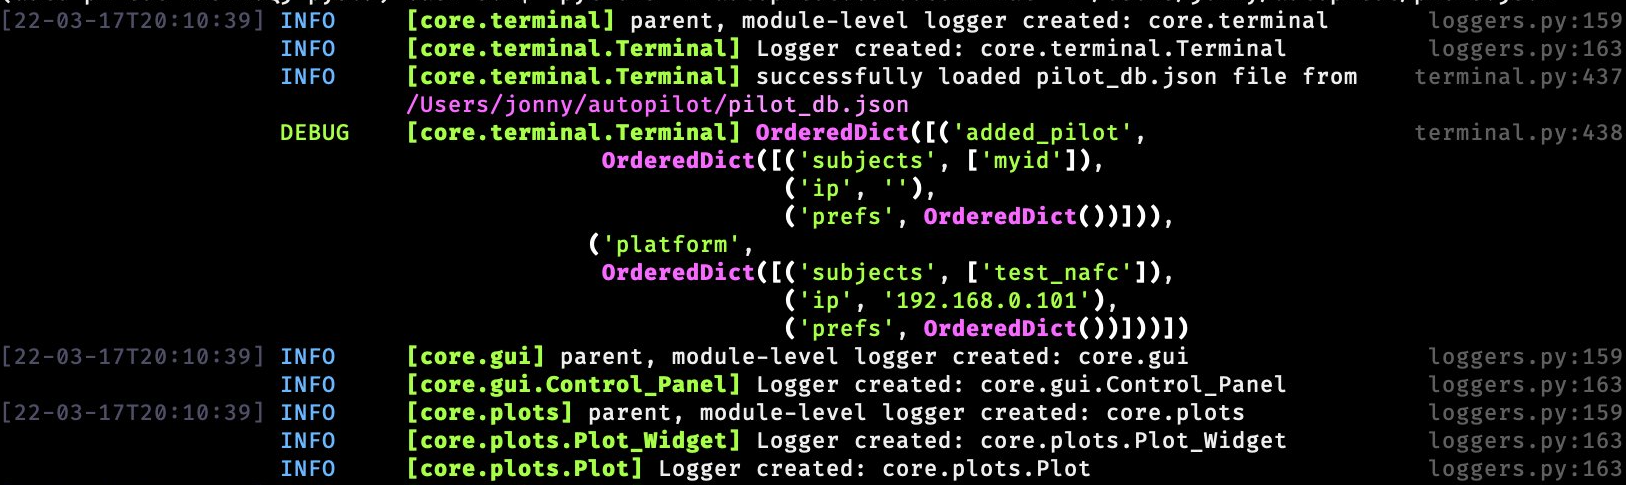
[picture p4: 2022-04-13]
autopilot/src/figures/logging.png

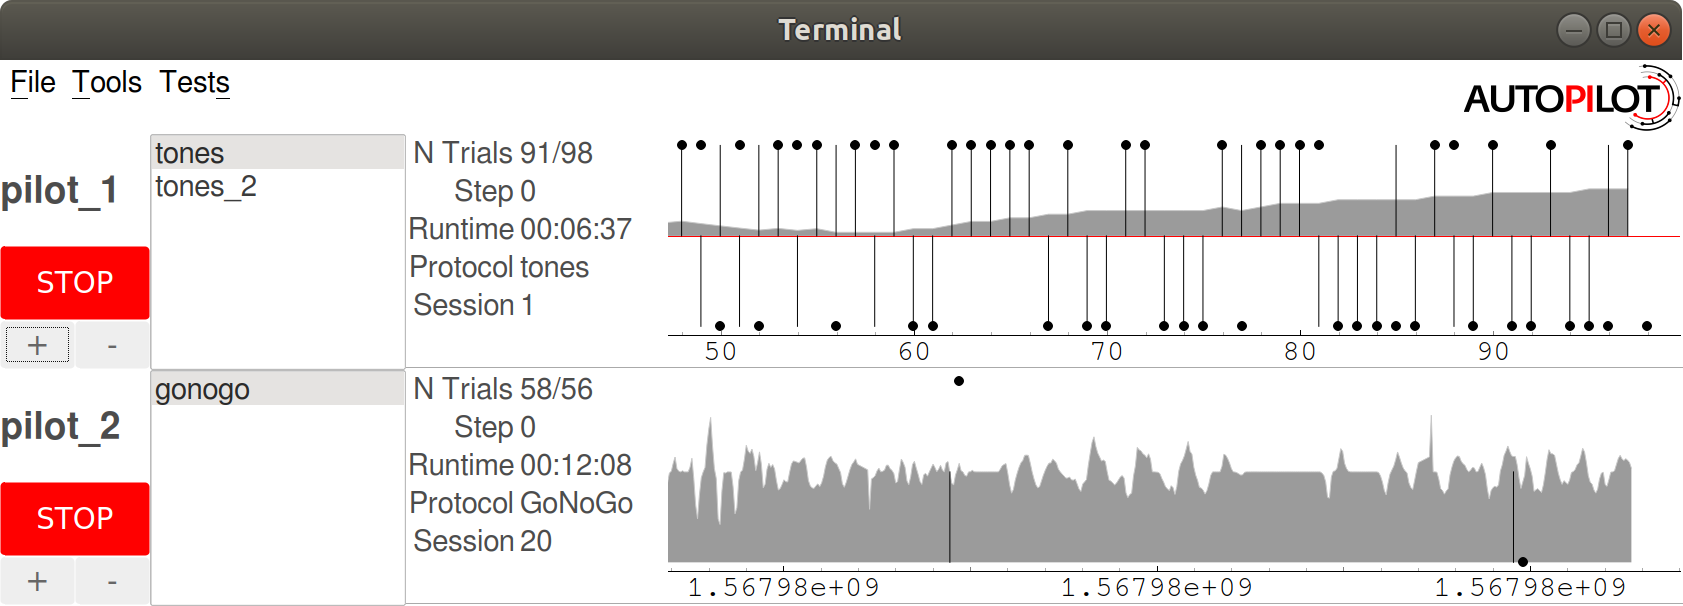
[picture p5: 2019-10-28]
autopilot/src/figures/ss_4.png

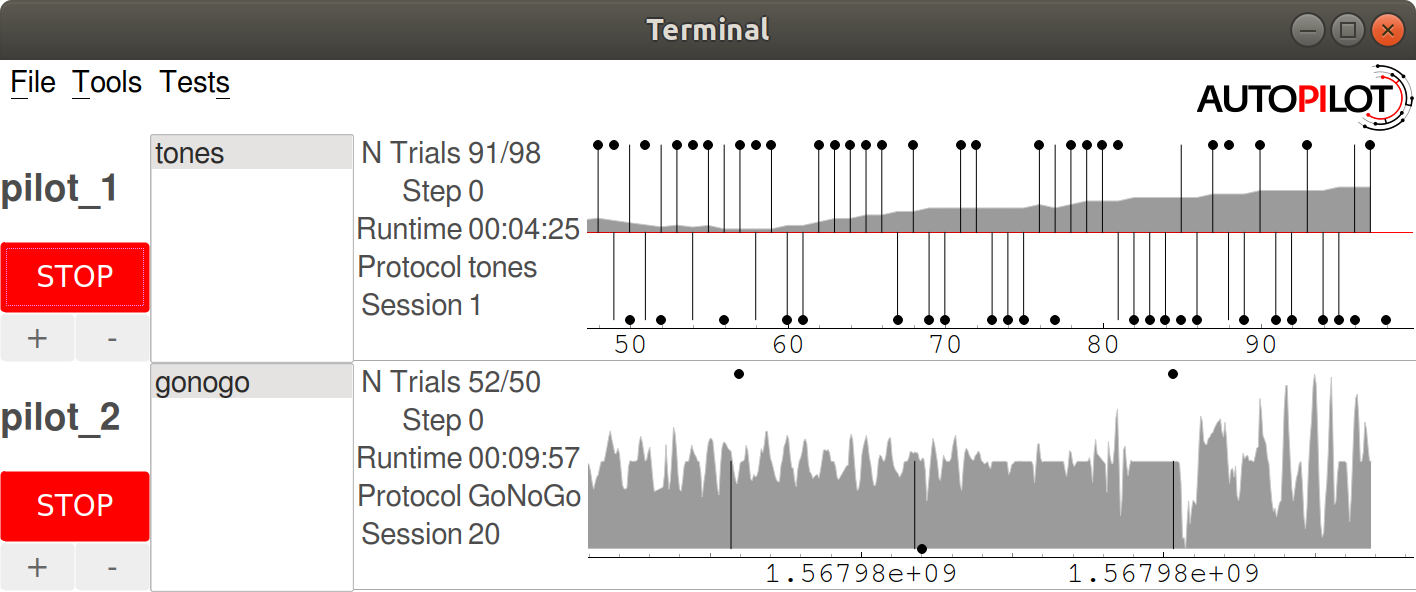
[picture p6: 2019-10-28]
autopilot/src/figures/ss_1.png

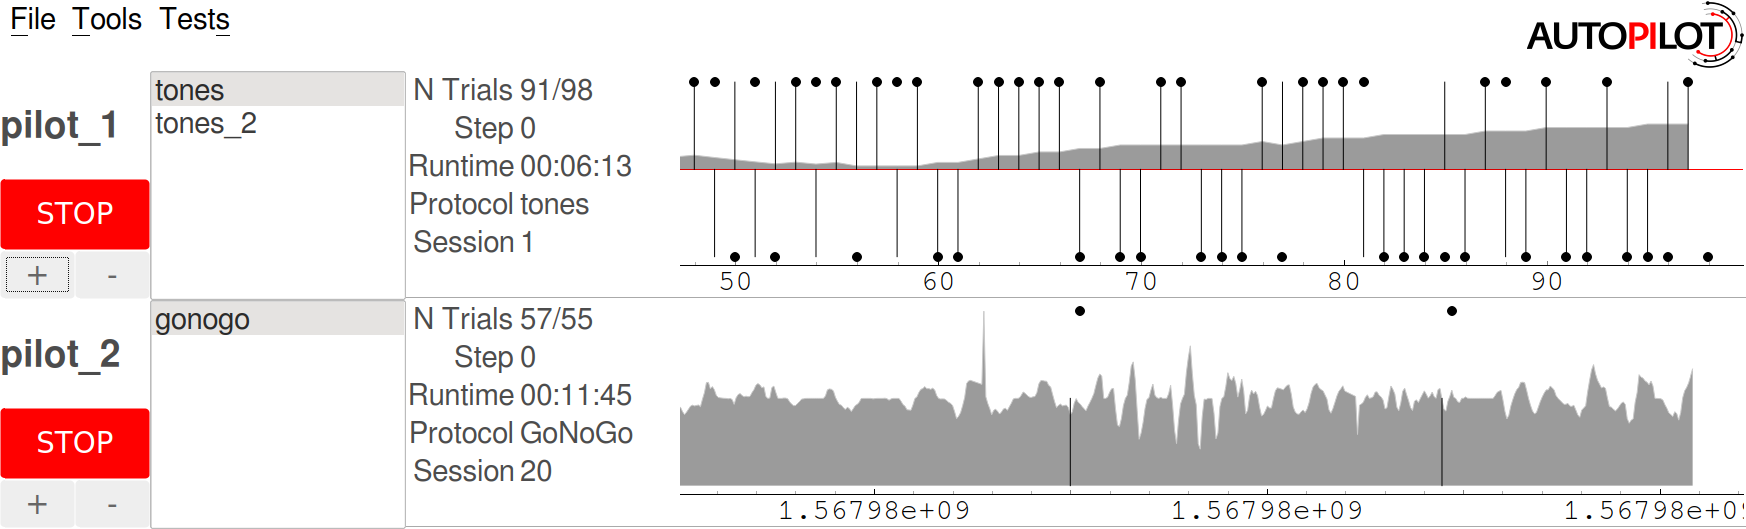
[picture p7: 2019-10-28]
autopilot/src/figures/ss_3.png

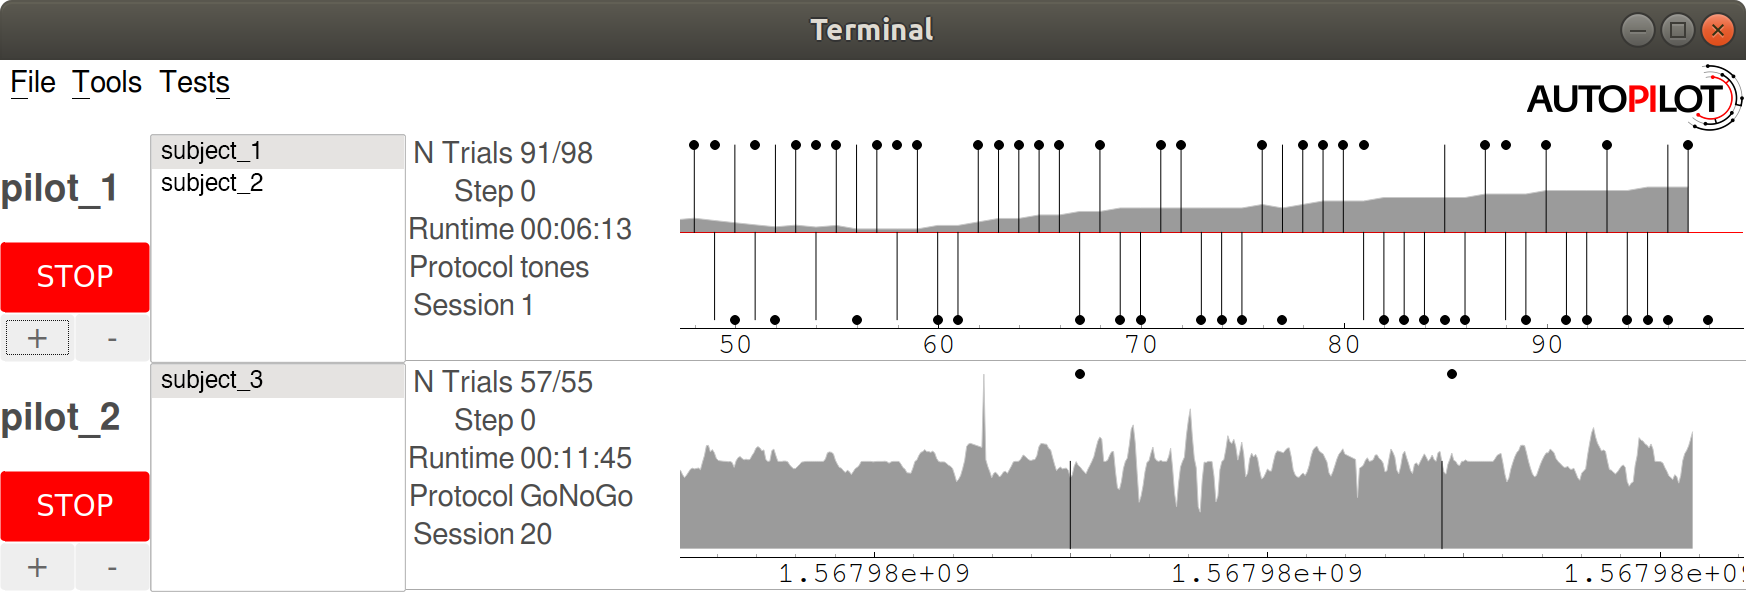
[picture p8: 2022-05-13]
autopilot/src/figures/ss_3_nocrop.png

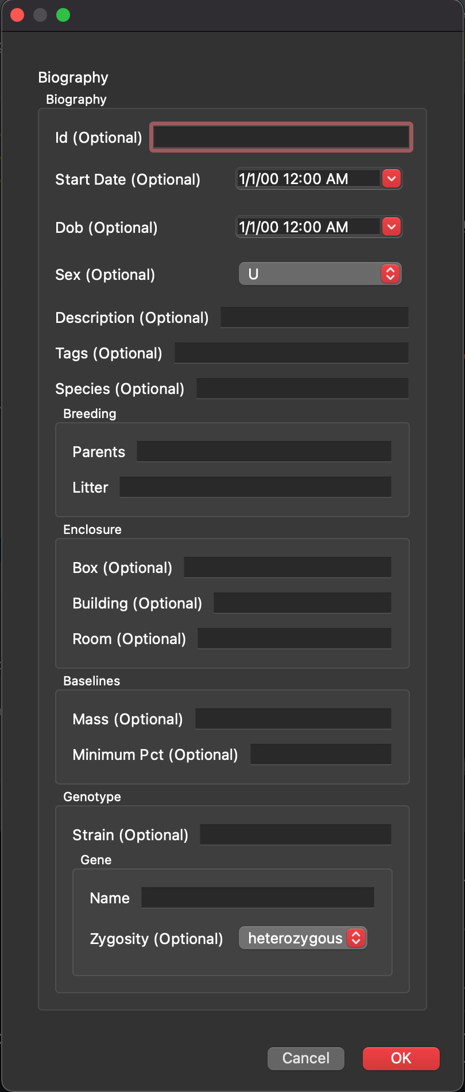
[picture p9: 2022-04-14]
autopilot/src/figures/model_form.png

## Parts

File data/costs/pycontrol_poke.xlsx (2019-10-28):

Electronic components
Part | Value | Device | Package | Description | MF | MPN | OC_FARNELL | price | link
IR_LED |  | - | - | IR LED side | Sharp | GL480E00000F | 9707794 | 0.5 | https://www.newark.com/sharp/gl480e00000f/ir-emitter-side-emit/dp/97K0541
PHOTO_TRAN |  | - | - | PHOTO TRANSISTOR | OSRAM | SFH3100F-1-Z | 1226443 | 0.75 | https://www.newark.com/osram-opto-semiconductors/sfh3100f-1-z/phototransistor-filtered/dp/05M1221?pf=810110302
LED |  | - | 0805 | LED white 0805 | MULTICOMP | OVS-0801 | 1716764 | 0.42 | https://www.newark.com/multicomp/ovs-0801/led-white-1-25mm-x-1-4mm-400mcd/dp/15R2209?ost=MULTICOMP%09OVS-0801&ddkey=https%3Aen-US%2FElement14_US%2Fsearch
R1 | 220R | - | 0805 | RESISTOR 0805 | MULTICOMP | MC01W08051220R | 9332804 |  | prices
R2 | 10K | - | 0805 | RESISTOR 0805 | MULTICOMP | MC01W0805510K | 9333720 |  | are
R3 | 150R | - | 0805 | RESISTOR 0805 | MULTICOMP | MC01W08051150R | 9332596 |  | negligible
SV1 |  | - | - | Receptacle | AMPHENOL FCI | 76341-307LF | 1098037 | 0.95 | https://www.mouser.com/ProductDetail/Amphenol-FCI/76341-307LF?qs=5xI8GKdkXlkQvFyqemiYYQ%3D%3D
RJ45 |  | RJ45VERTICAL | RJ45VERTICAL | RJ45VERTICAL | TE CONNECTIVITY | 5556416-1 | 1773034 | 0.93 | https://www.te.com/usa-en/product-5556416-1.html
solenoid |  |  |  |  |  |  |  | 68 | https://sites.google.com/site/bpoddocumentation/bill-of-materials
 |  |  |  |  |  |  |  | 71.55

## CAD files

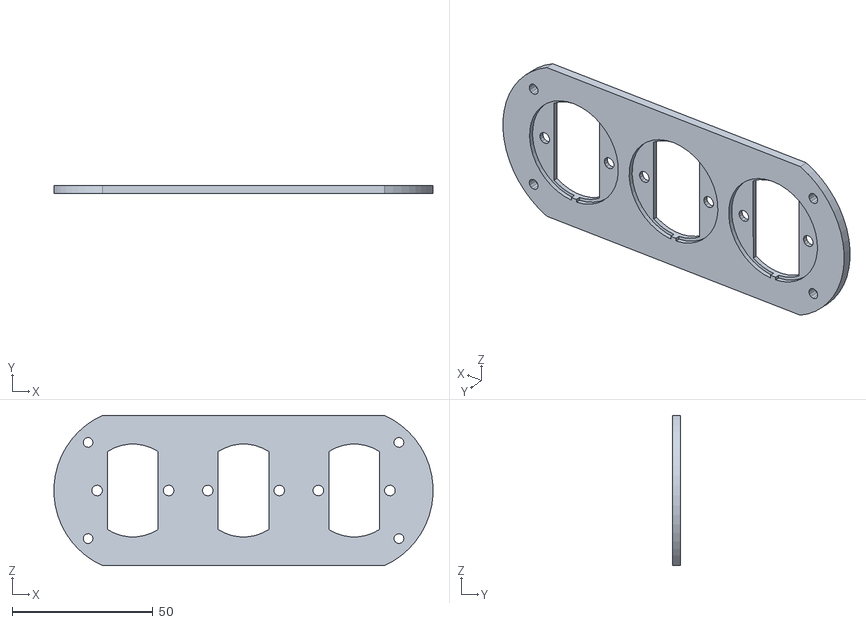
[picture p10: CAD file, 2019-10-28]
autopilot/src/figures/porthole_lowpoly.stl
134.5 x 3.00 x 53.4

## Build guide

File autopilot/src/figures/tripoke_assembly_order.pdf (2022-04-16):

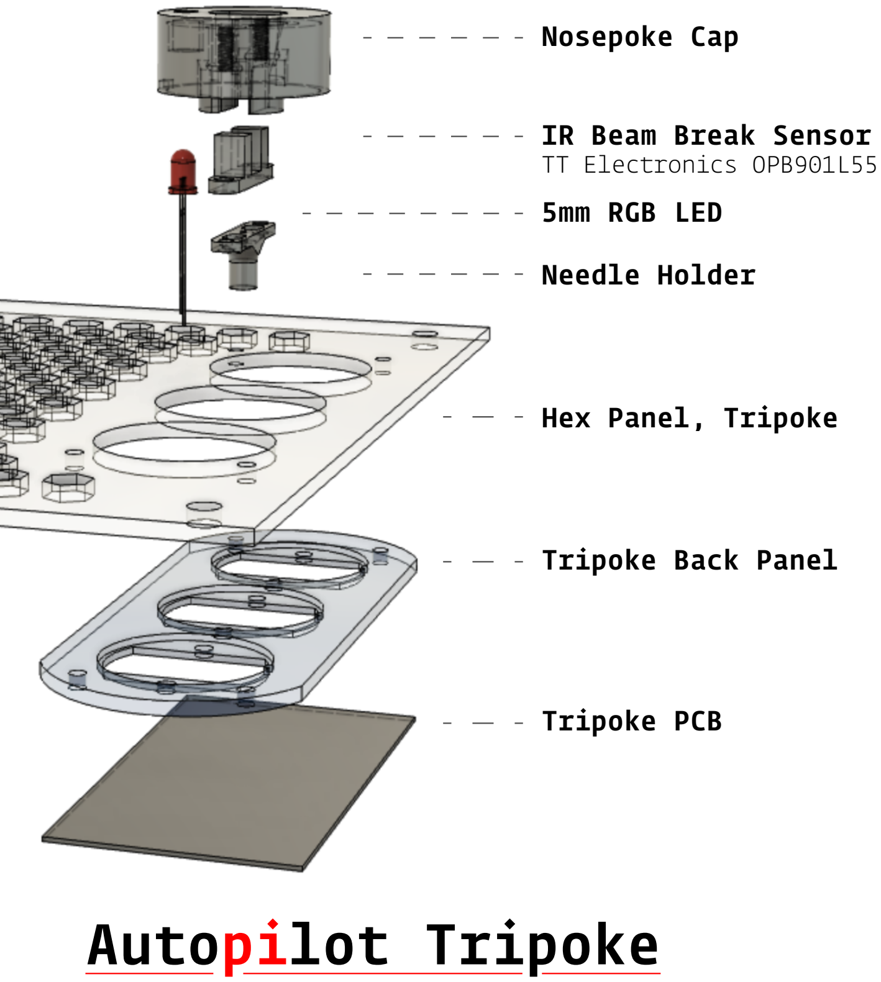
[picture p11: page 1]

Nosepoke Cap

IR Beam Break Sensor
TT Electronics OPB901L55
5mm RGB LED

Needle Holder

Hex Panel, Tripoke

Tripoke Back Panel

Tripoke PCB

# Autopilot Tripoke

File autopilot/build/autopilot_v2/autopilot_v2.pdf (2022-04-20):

## Autopilot

Automating behavioral experiments with lots of Raspberry Pis

### JONNY L. SAUNDERS, MICHAEL WEHR @ April 19, 2022

Neuroscience needs behavior, and behavioral experiments require the coordination of large numbers of heterogeneous hardware components and data streams. Currently available tools strongly limit the complexity and reproducibility of experiments. Here we introduce Autopilot, a complete, open-source Python framework for behavioral neuroscience that distributes experiments over networked swarms of Raspberry Pis. Autopilot enables qualitatively greater experimental flexibility by allowing arbitrary numbers of hardware components to be combined in arbitrary experimental designs. Research is made reproducible by documenting all data and task design parameters in a human-readable and publishable format at the time of collection. Autopilot provides an order-of-magnitude performance improvement over existing tools while also being an order of magnitude less costly to implement. Autopilot’s flexible, scalable architecture allows neuroscientists to design the next generation of experiments to investigate the behaving brain.

version: v2-18-ge9f406d

H O M E PAG E (https://auto-pi-lot.com)

R E P O S I T O R Y (https://github.com/wehr-lab/autopilot)

D O C U M E N TAT I O N (https://docs.auto-pi-lot.com)

# Contents

1 Introduction | 5
1.1 Existing Systems for Behavioral Experiments | 7
1.2 Limitations of Existing Systems | 8
2 Design | 11
2.1 Efficiency | 11
2.2 Flexibility | 13
2.3 Reproducibility | 15
3 Program Structure | 19
3.1 Directory Structure | 19
3.2 Data | 20
3.3 Tasks | 22
3.4 Hardware | 27
3.5 Transforms | 28
3.6 Stimuli | 29
3.7 Agents | 29
3.8 Networking | 31
3.9 GUI & Plots | 33
4 Tests | 35
4.1 Latency | 35
4.2 Bandwidth | 36
4.3 Distributed Go/No-go Task | 37

4 jonny l. saunders, michael wehr @

5 Limitations and Future Directions | 39
6 Glossary | 41
Bibliography | 45

1

# Introduction

Animal behavior experiments need precision and patience, so we make computers do them for us. The complexity of contemporary behavioral experiments, however, presents a stiff methodological challenge. For example, researchers might wish to measure pupil dilation[41, 41], respiration[37], and running speed[36], while tracking the positions of body parts in 3 dimensions[35] and recording the activity of large ensembles of neurons[24], as subjects perform tasks with custom input devices such as a steering wheel[9] while immersed in virtual reality environments using stimuli synthesized in real time[50, 11]. Coordinating the array of necessary hardware into a coherent experimental design—with the millisecond precision required to study the brain—can be daunting.
Historically, researchers have developed software to automate behavior experiments as-needed within their lab or relied on purchasing proprietary software (eg. [16]). Open-source alternatives have emerged recently, often developed in tandem with hardware peripherals available for purchase [18, 43]. However, the diverse hardware and software requirements for behavioral experiments often lead researchers to cobble together multiple tools to perform even moderately complex experiments. Understandably, most software packages do not attempt to simultaneously support custom hardware operation, behavioral task logic, stimulus generation, and data acquisition. The difficulty of designing and maintaining lab-idiosyncratic systems thus defines much of the everyday practice of science. Idiosyncratic systems can hinder reproducibility, especially if the level of detail reported in a methods section is sparse[53]. Additionally, development time and proprietary software are expensive, as are the custom hardware peripherals that are required to use most available open-source behavior software, stratifying access to state-of-the-art techniques according to inequitable funding distributions.
Technical challenges are never merely technical: they reflect and are structured by underlying social challenges in the organization of scientific labor and knowledge work. Lab infrastructure occupies a space between technology intended for individual users and for large organizations: that of groupware¹
[21, 22]. Experimental 1
“Our original definition of groupware was ‘intentional group processes plus software to support them.’ It has both computer and human components: software of the computer and ‘software’ of the people using it. [...] Recently this definition has been extended to include other more expressly cultural factors including myth, values and norms. The computer software should reflect and support a group’s purpose, process and culture.”
Peter and Trudy Johnson-Lenz (1991)[22] frameworks then face the joint challenge of technical competency while also embedding in and supporting existing cultures of practice. Behind every line of code is an unwritten wealth of technical knowledge needed to make use of it, as well as an unspoken set of beliefs about how it is to be used — labs aren’t born fresh on release day ready to retool at a moment’s notice, they’re held together by decades of duct tape and run on ritual. The boundaries of this “contextual knowledge” extend fluidly beyond individual labs, structuring disciplinary, status, and role systems in scientific work[7]. Given their position at the intersection of scientific theory, technical work, data production, and social organization; experimental frameworks are an elusive design challenge: but also an underexplored means of realizing some of our loftier dreams of open, accessible, and collaborative science.

Here we present Autopilot, a complete open-source software and hardware frame-

6 autopilot automating behavioral experiments with lots of raspberry pis

work for behavioral experiments. We leverage the power of distributed computing
using the surprisingly capable Raspberry Pi 4²
to allow researchers to coordinate ar- 2
See Table 3.2
bitrary numbers of heterogeneous hardware components in arbitrary experimental designs.
Autopilot takes a different approach than existing systems to overcome the technical challenges of behavioral research: just use more computers. Specifically, the advent of inexpensive single-board computers (ie. the Raspberry Pi) that are powerful enough to run a full Linux operating system allows a unified platform to run on every Pi or other computer in the system so that they can work together seamlessly. At the core of its architecture is a networking protocol (Section 3.8) that is fast enough to stream electrophysiological or imaging data and flexible enough to make the mutual coordination of hardware straightforward.
This distributed design also makes Autopilot extremely scalable, as the Raspberry Pi’s $35 price tag makes it an order of magnitude less costly than comparable systems (Section 2.3). Its low cost doesn’t come at the expense of performance or useability: Autopilot also has an order of magnitude greater measurement precision and an order of magnitude lower latency than comparable systems (Sections 2.1 and 4). Autopilot balances experimental flexibility with support. Its task design infrastructure is flexible enough to perform arbitrary experiments, but also provides support for data management, plotting task progress, and custom training regimens. We try to bridge multiple modalities of use: use its modular framework of tools out of the box, or use its complete low-level API documentation³ (https://docs.auto-pi-lot.com)
to hack at it until it does 3
https://docs.auto-pi-lot.com
what you need. Rather than relying on costly proprietary hardware modules, users can take advantage of the wide array of peripherals and extensive community support available for the Raspberry Pi. Autopilot is designed to be permissive: build your whole experiment with it or just use its networking modules, adapt it to existing hardware, integrate your favorite analysis tool. We want Autopilot to play nice with other software libraries and existing practices, rather than forcing you to retool your lab around it.
Finally, we have designed Autopilot to help scientists do reproducible research and be good stewards of the human knowledge project. Experiments are not written as scripts that are reliant on the particularities of each researcher’s hardware configuration. Instead, we have designed the system to encourage users to write reusable, portable experiments that can be incorporated into a public central library while also allowing space to iterate and refine without needing to learn complicated programming best-practices to contribute. Every parameter that defines an experiment is automatically saved in publication-ready format, removing ambiguity in reported methods and facilitating exact replication with a single file. Its plugin system is built atop a densely-linked semantic wiki⁴ (https://wiki-auto-pi-lot.com)
that fluidly combines human- and computer- 4
https://wiki.auto-pi-lot.com
readable, communally editable technical knowledge that surrounds your experiments
with the software that performs them.

We begin by defining the requirements of a complete behavioral system and evalu- We would like to acknowledge and thank Lucas
Ott for doing much of the behavioral training, Brynna Paros and Nick Sattler for their help with constructing our behavioral boxes, Matt Smear and Reese Findley for loaning us their Bpod for far longer than they intended to, Erik Flister whose Ratrix software inspired some of the design features of Autopilot [33], several artists on flaticon.com (https://www.biorxiv.org/content/10.1101/807693v1flaticon.com) (Freepik, (https://www.flaticon.com/authors/freepik) Nikita Golubev, (https://www.flaticon.com/authors/nikita-golubev) Those Icons) (https://www.flaticon.com/authors/those-icons) whose work served as stems for many of the figures, and the Janet Smith House for the endless support and relentless criticism of the figures. This material is based on work supported by NIH NIDCD R01 DC-015828, NSF Graduate Research Fellowship No. 1309047, and a University of Oregon Incubating Interdisciplinary Initiatives award.

ating two current examples (Sections 1.1 and 1.2). We then describe Autopilot’s design principles (Section 2) and how they are implemented in the program’s structure (Section 3). We close with a demonstration of its current capabilities and our plans to expand them (Sections 4 and 5).

introduction 7

### 1.1 Existing Systems for Behavioral Experiments

At minimum, a complete system to automate behavioral experiments has 6 requirements:

1. Hardwareto interact with the experimental subject, including sensors (eg. pho-Hardware
todiodes, cameras, rotary encoders) to receive input and actuators (eg. lights, motors, solenoids) to provide feedback.
2. Some capability to synthesize and present sensory stimuli. Ideally both discrete Stimuli
stimuli, like individual tone pips or grating patches, and continuous stimuli, like those used in virtual reality experiments, should be possible.
3. A framework to coordinate hardware and stimuli as a task. Task definition Tasks
should be flexible such that it facilitates rather than constrains experimental design.
4. Adata managementsystem that allows fine control of data collection and format. Data
Data should be human readable and include complete metadata that allows independent analysis and reproduction. Ideally the program would also allow some means of realtime data processing of sensor values for use in a task.
5. Some means of visualizing dataas it is collected in order to observe task status. It Visualization
should be possible to customize visualization to the needs and structure of the task.
6. Finally, a user interfaceto control task operation. The UI should make it possible UI
for someone who does not program to operate the system.

We will briefly describe two other systems that are “complete” as described above:

Included Partial/Limited

pyControl and Bpod.

pyControl

pyControl[3] (https://pycontrol.readthedocs.io/en/latest/) is a behavioral framework built in Python by the Champalimaud FounpyControl

hardware

stimuli

tasks
data

viz

UI

dation. It uses the micropython microcontroller (https://micropython.org/) (“pyboard”) as its primary hardware device along with several extension boards sold by openephys. (http://www.open-ephys.org/store/pycontrol) The pyboard has four I/O ports, or eight with a multiplexing expander board. Schematics are available for many other hardware components like solenoid valve drivers and rotary encoders. Multiple pyboards can be connected to a computer via USB and run independent tasks simultaneously with a GUI.
There is limited support for some parametrically defined sound stimuli, presented from a separate amplifier connected using the I2C protocol. Visual stimuli are unsupported.
Like most behavioral software, pyControl uses a finite-state machine formalism to define its tasks. A task is a set of discrete states, each of which has a set of events that transition the task from one state to another. pyControl also allows timed transitions between states, and one function that is called on every event for a rough sort of parallelism. pyControl also allows the use of external variables to control state logic, making these state machines more flexible than strict finite state machines.

D 0 2
D 8976 3
D 8976 1
P 8976 Print Statement
D 10162 3
D 10163 2
Figure 1.1: pyControl data is stored as plain text, each line having a type (like Data or Print), timestamp, and state

8 autopilot automating behavioral experiments with lots of raspberry pis

All events and states are stored alongside timestamps as a plain text log file, one file
per subject per session (Figure 1.1). Anlog data are stored in a custom binary serialization that alternates 4-byte data and timestamp integers.
There is only one plot type available in the GUI, a raster plot of events, and no facility for varying the plot by task type. The GUI is otherwise quite capable, including the ability to batch run subjects, redefine task variables, and configure hardware.

Bpod

Bpod is primarily a collection of hardware designs and an assembly service run by Bpod

hardware
stimuli

tasks
data

viz

UI

Sanworks LLC. (https://www.sanworks.io/about/about.php) Similar to pyControl, each Bpod behavior box is based on a finite-state machine microcontroller with four I/O ports. Additional hardware modules provide extended functionality. Bpod is controlled using its own MATLAB package, (https://github.com/sanworks/Bpod_Gen2) though there are at least two other third-party software packages, BControland (https://brodylabwiki.princeton.edu/bcontrol/index.php/Main_Page) pyBpod, (https://pybpod.github.io/) that can control Bpod hardware. A task is implemented as a MATLAB script that constructs a new state machine for each trial, uploads it to the Bpod, and waits for the trial to finish. As a result, only one Bpod can be used per host computer, or at least per MATLAB session. Data are stored as trial-split events in a MATLAB structure.
There are a few basic plots for two-alternative forced choice tasks, but there doesn’t seem to be a prescribed way to add additional plots. Bpod has a reasonably complete GUI for managing the hardware and running tasks, but it is relatively technical (Figure 1.2).

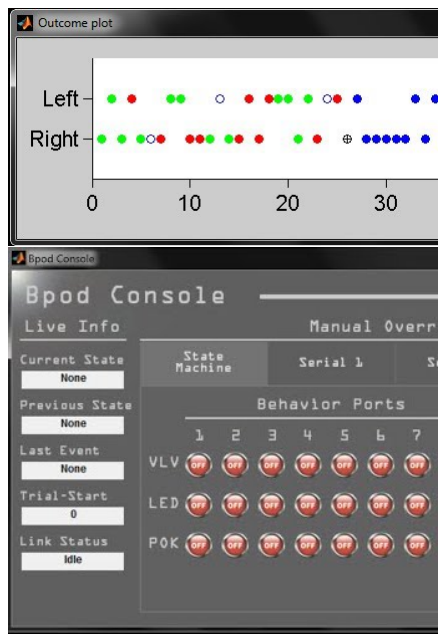
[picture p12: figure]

Figure 1.2: A Bpod event plot (above) showing the results of individual behavioral trials, and the Bpod GUI (below).

For brevity we have omitted many other excellent tools that perform some subset of the operations of a complete behavioral system, or are otherwise have a substantial difference in scope.⁵

5 Other tools:
- Bonsai[30] - site, (https://bonsai-rx.org/) git (https://github.com/bonsai-rx/bonsai)
- Expyriment[28] - site, (https://www.expyriment.org/) git (https://github.com/expyriment/expyriment.git)
- PsychoPy[40] - site, (https://www.psychopy.org/) git (https://github.com/psychopy/psychopy)
- OpenSesame[31] - site, (https://osdoc.cogsci.nl/) git (https://github.com/smathot/OpenSesame)
- SMiLE - docs (https://smile-docs.readthedocs.io/en/latest/)
- ArControl[12] - git (https://github.com/chenxinfeng4/ArControl)
- and see OpenBehavior (http://openbehavior.com/)

### 1.2 Limitations of Existing Systems

We see several limitations with these and other behavioral systems:

- Hardware - Both Pycontrol and Bpod strongly encourage users to purchase a limited set of hardware modules and add-ons from their particular hardware ecosystem. If a required part is not available for purchase, neither system provides a clear means of interacting with custom hardware, requiring the user to ’tack on’ loosely-integrated components. There is also a hard limit on the number of hardware peripherals that can be used in any given task, as there is no ability to use additional pyboards or Bpod state machines. The microcontrollers used in these systems also impose strong limits on their software: neither run a full, high-level programming language⁶
. We will discuss this further in section 2.2. A

6 Bpod runs custom firmware (https://github.com/sanworks/Bpod_StateMachine_Firmware) written in C++ on a Teensy 3.6 (https://www.pjrc.com/store/teensy36.html) microcontroller. pyControl’s pyboard implements micropython, (https://micropython.org/) a subset of Python that excludes canonical libraries like numpy[51] or scipy[23]

broader limitation of existing systems is the difficulty of flexibly integrating the diverse hardware and analytical tools necessary to perform the next generation of behavioral neuroscience experiments that study “naturalistic, unrestrained, and minimally shaped behavior”[14].
- Stimuli - Stimuli are not tightly integrated into either of these systems, requiring

introduction 9

the user to write custom routines for their synthesis, presentation, and description in the resulting data. Neither are capable of delivering visual stimuli. Since the publication of the initial version of this manuscript, Bpod has added support for the HiFiberry that we also describe here[44], but the sound generation API appears to be unchanged, (https://github.com/sanworks/Bpod_Gen2/blob/df6cd0c7d5df8247b02077b05fc263f79b86b096/Examples/Protocols/Sound/HiFiSound2AFC_TrialManager/HiFiSound2AFC_TrialMan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) with a single method for generating sine waves. (https://github.com/sanworks/Bpod_Gen2/blob/1cb181dffbb7394acd18819f1d268fd9dec6ec5b/Functions/Internal%20Functions/GenerateSineWave.m) Some parametric audio stimuli are included in the pyControl source code (https://bitbucket.org/takam/pycontrol/src/default/pyControl/audio.py) but we were unable to find any documentation or examples of their use.

for currentTrial = 1:MaxTrials % new state matrix every trial sma = NewStateMatrix();

% add states and transitions sma = AddState(sma,
'Name', 'Wait', ...
'Timer', 0,...
'StateChangeConditions', ... {'Port2In', 'Delay'}, ...
'OutputActions', ...
{'AudioPlayer1','*'});
% add more states...

% upload and run task
SendStateMatrix(sma);
RawEvents = RunStateMatrix;

% manually gather data and params BpodSystem.Data = AddTrialEvents( BpodSystem.Data, RawEvents);

% plotting in the main loop UpdateSideOutcomePlot(...); UpdateTotalRewardDisplay(...);

% manually save data
SaveBpodSessionData;
end
Figure 1.3: Bpod’s general task structure. (https://github.com/sanworks/Bpod_Gen2/blob/master/Examples/Protocols/AnalogSound2AFC/AnalogSound2AFC.m)
- Tasks - Tasks in both systems require a large amount of code and effort duplication. Neither system has a notion of reusable tasks or task ’templates,’ so every user needs to rewrite every task from scratch. Bpod’s structure in particular tends to encourage users to write long task scripts (https://github.com/sanworks/Bpod_Gen2/blob/df6cd0c7d5df8247b02077b05fc263f79b86b096/Examples/Protocols/Sound/AnalogSound2AFC/AnalogSound2AFC.m) that are difficult to read (Figure 1.3) because much of its codebase is ’backend’ code for compiling and communicating with the state machine, so users have to write basic routines like stimulus creation themselves. Another factor that contributes to the difficulty of task design in these systems is the need to work around the limitations of finite state machines, which we discuss further in section 3.3.
- Data - Data storage and formatting is basic, requiring extensive additional processing to make it human readable. For example, to determine whether a subject got a trial correct in an example (https://github.com/sanworks/Bpod_Gen2/blob/master/Examples/Protocols/Light/Light2AFC/Light2AFC.m) Bpod experiment, one would use the following code:

SessionData.RawEvents.Trial{1,1}.States.Punish(1) ~= NaN
As a result, data format is idiosyncratic to each user, making data sharing dependent on manual annotation and metadata curation from investigators.
- Visualization & GUI - The GUIs of each of these systems are highly technical, and are not designed to be easily used by non-programmers, though pyControl’s documentation offsets much of this difficulty. Visualization of task progress is quite rigid in both systems, either a timeseries of task states or plots specific to two-alternative forced choice tasks. There is no obvious way to adapt plots to specific tasks.
- Documentation - Writing good documentation is challenging, but particularly for infrastructural systems where a user is likely to need to modify it to suit their needs it is important that it be possible to understand its lower-level workings. PyControl has relatively good user documentation (https://pycontrol.readthedocs.io/en/latest/) for how to use the system, but no API-level documentation. Bpod’s documentation (https://sites.google.com/site/bpoddocumentation/home) is a bit more scattered, and though it does have documentation for asubset of its functions, (https://sites.google.com/site/bpoddocumentation/user-guide/function-reference) there is little indication of how they work together or how someone might be able to modify them.
- Reproducibility - As of November 2020, (https://github.com/pyControl/code/blob/cc6e7ab67c18388dea85b3ac48ac66a65ffa12f8/ChangeLog.txt#L74) pyControl has versioned task files (https://pycontrol.readthedocs.io/en/latest/user-guide/pycontrol-data/#versioned-task-files) that append a hash to each version of a task and save it along with any produced data. PyControl’s most recent releases have explicit version numbers, (https://github.com/pyControl/code/releases) but these don’t appear to be saved along with the data. Bpod stores neither code nor task versions in its data. Neither system saves experimental parameter changes by default —and the GUIs of both allow parameters to be changed at will— and so critical data could be lost and experiments made unreproducible unless the user writes custom code to save them. Bpod has an undocumented plugin system, (https://github.com/sanworks/Bpod_Gen2/commit/10ad997555086afb93dfc1080091acaa58d740f9) but neither system has a formal system for sharing plugins or task code, requiring work to be duplicated across all users of the system.

10 autopilot automating behavioral experiments with lots of raspberry pis

- Integration and Extension - Integration with other systems that might handle some out-of-scope function is tricky in both of these example systems. All
systems have some limitation, so care must be taken to provide points by which other systems might interact with them. One particularly potent example is the use of Bpod in the International Brain Laboratory’s standardized experimental rig[29], which relies on a single-purpose 93 page PDF (https://figshare.com/articles/preprint/A_standardized_and_reproducible_method_to_measure_decision-making_in_mice_Appendix_3_IBL_protocol_for_setting_up_the_be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) to describe how to use the iblrig (https://github.com/int-brain-lab/iblrig) library, which consists of a large amount of single-purpose code for stitching together pybpod with bonsai (https://github.com/int-brain-lab/iblrig/blob/18569278fc2d8cd3266adb2a5f660a43f8f2582e/iblrig/bonsai.py) for controlling video acquisition. Even if a system takes that amount of additional work to integrate with another, hopefully the system allows it to be done in a way such that it can be reused and shared with others in the future so they can be spared the trouble. The relatively sparse documentation (https://iblrig.readthedocs.io/en/latest/index.html) and the high proportion of ibl-specific code present in the repository make that seem unlikely.

Some of these limitations are cosmetic—fixable with additional code or hardware— but several of the most crucial are intrinsic to the design of these systems.
These systems, among others, have pioneered the development of modern behavioral hardware and software, and are to be commended for being open-source and highly functional. One need look no further for evidence of their usefulness than to their adoption by many labs worldwide. At the time that these systems were developed, a general-purpose single-board computer with performance like the Raspberry Pi 4 was not widely available. The above two systems are not unique in their
limitations, but are reflective of broader constraints of developing experimental tools. And Autopilot, of course, also has many of its own We are only able to articulate the design principles that differentiate Autopilot by weaknesses
building on their work.

2

# Design

Autopilot distributes experiments across a network of Raspberry
Pis,¹
a type of inexpensive single-board computer. | 1 Raspberry Pi model 4B, (https://www.raspberrypi.org/products/raspberry-pi-4-model-b/) see Table 3.2

Autopilot has three primary design principles:

1. Efficiency - Autopilot should minimize computational overhead and maximize
use of hardware resources.
2. Flexibility - Autopilot should be transparent in all its operations so that users can expand it to fit their existing or desired use-cases. Autopilot should provide clear points of modification and expansion to reduce local duplication of labor to compensate for its limitations.
3. Reproducibility - Autopilot should maximize system transparency and minimize the potential for the black-box of local reprogramming. Autopilot should maximize the information it stores about its operation as part of normal data collection.

### 2.1 Efficiency

Though it is a single board, the Raspberry Pi operates more like a computer than a microcontroller. It most commonly runs a custom Linux distribution, Raspbian, allowing Autopilot to use Python across the whole system. Using an interpreted language like Python running on Linux has inherent performance drawbacks compared to compiled languages running on embedded microprocessors. In practice these drawbacks are less profound than they appear on paper: Python’s overhead is negligible on modern processors²
, jitter and performance can be improved by wrap- 2
| and improvements to CPython in Python 3.11
and onwards will bring overhead close to zero[4] ping compiled code, etc. While we view the gain in accessibility and extensibility of a widely used high-level language like Python as outweighing potential performance gains from using a compiled language, Autopilot is nevertheless designed to
maximize computational efficiency.

Concurrency

time

cpu0

wait for poke

deliver water
plot result

Figure 2.1: A single-threaded program executes all operations sequentially, using a single process and cpu core.

Most behavioral software is single-threaded (Figure 2.1), meaning the program will only perform a single operation at a time. If the program is busy or waiting for an input, other operations are blocked until it is finished.
Autopilot distributes computation across multiple processes and threads to take advantage of the Raspberry Pi’s four CPU cores. Every object in Autopilot does its work in separatethreads. Specifically, Autopilot spawns separate threads to process messages and events, an architecture described more fully in section 3.8. Threading does not offer true concurrency³
, but does allow Python to distribute computa-

3

See David Beazley’s ’Understanding the Global Interpreter Lock’ (http://www.dabeaz.com/python/UnderstandingGIL.pdf) and associated visualizations. (http://www.dabeaz.com/GIL/gilvis/index.html)

12 autopilot automating behavioral experiments with lots of raspberry pis

tional time between operations so that, for example, waiting for an event does not
block the rest of the program, and events are not missed because the program is busy
(Figure 2.2).

time

cpu0

wait for poke

plot result

compute next stage

deliver water

waiting

Figure 2.2: A multi-threaded program divides computation time of a single process and cpu core across multiple operations so that, for example, waiting for input doesn’t block other operations.

Critical operations that are computationally intensive or cannot be interrupted are given their own dedicated processes. Linux allows individual cores of a processor to be reserved for single processes, so individual Raspberry Pis are capable of running four truly parallel processing streams. For example, all Raspberry Pis in anAutopilot swarm create a messaging client to handle communication between devices which runs on its own processor core so no messages are missed. Similarly, if an experiment requires sound delivery, a realtime sound engine in a separate process (Figure 2.3) also runs on its own core.
Since even moderately complex experiments can consume more resources than are available on a single processor, the topmost layer of concurrency in Autopilot is to use additional computers. Autopilot uses the Raspberry Pi as a low-cost hardware controller, but only its GPIO control system is unique to them: the rest of the code can be used on any type of computer, so computationally expensive or GPUintensive operations can be offloaded to any number of high performance machines. Computers divide labor autonomously (see ?? and 3.7 ), so for example a computer running a task can send and receive messages from one running the GUI and plots, but does not depend on that input as it would in a system that couples a microcontroller with a managing computer. The ability to coordinate multiple, autonomous computers with heterogeneous responsibilities and capabilities in a shared task is Autopilot’s definitive design decision.
time
cpu1 | play sound
cpu2 | process | messages

Figure 2.3: A multi-process program is truly concurrent, allowing multiple cpu cores to operate
in parallel. Leveraging Low-Level Libraries

Autopilot uses Python as a “glue” language, where it wraps and coordinates faster
low-level compiled code[52]. Performance-critical components of Autopilot are
thin wrappers around fast C libraries (Table 2.1). As Autopilot’s API matures, we
intend to replace any performance-limiting Python code like its sound server and networking operations with compiled code exposed to python with tools like the C Foreign Function Interface (CFFI). (https://cffi.readthedocs.io/en/latest/index.html)

Table 2.1: A few libraries Autopilot uses jack (http://jackaudio.org/) realtime audio
pigpio (http://abyz.me.uk/rpi/pigpio/index.html) GPIO control
ZeroMQ (http://zeromq.org/) networking
Qt (https://www.qt.io/) GUI

Since Autopilot coordinates its low-level components in parallel rather putting everything inside one “main loop,” Autopilot actually has better temporal resolution than single-threaded systems like Bpod or pyControl, despite the realtime nature of their dedicated processors (Table 2.2).

Table 2.2: Using pigpio as a dedicated I/O process gives autopilot greater measurement precision Precision
Autopilot (pigpio) (http://abyz.me.uk/rpi/pigpio/pigpiod.html) | 5µs
Bpod (https://github.com/sanworks/Bpod_StateMachine_Firmware/blob/059d1e9195f5bb7d0d5cd7b33f56342eb5a3a55c/Dev/StateMachineFirmware/StateMachineFirmware.ino) | 100µs
pyControl (https://bitbucket.org/takam/pycontrol/src/c678552ac57be2108a5461e0c5f8051ce7d3816a/pyControl/framework.py?at=default&fileviewer=file-view-default) | 1000µs

Caching

Finite-state machines are only aware of the current state and the events that transition it to future states. They are thus incapable of exploiting the often predictable structure of behavioral tasks to precompute future states and precache stimuli. Further, to change task parameters between trials (eg. changing the rewarded side in a two-alternative forced-choice task), state machines need to be fully reconstructed and reuploaded to the device that runs them each time.
Autopilot precomputes and caches as much as possible. Rather than wait “inside” a state, Autopilot prepares each of the next possible events and saves them for immediate execution when the appropriate trigger is received. Static stimuli are prepared

design 13

once at the beginning of a behavioral session and stored in memory. Before their presentation, they are buffered to minimize latency.
By providing full low-level documentation, we let researchers choose the balance between ease of use and performance themselves: it’s possible to just call a sound’s play() (https://docs.auto-pi-lot.com/en/latest/stim/sound/base.html) method, explicitly buffered with its buffer() (https://docs.auto-pi-lot.com/en/latest/stim/sound/base.html) method, or generated on the fly with its play_continuous() (https://docs.auto-pi-lot.com/en/latest/stim/sound/base.html) method. Similarly, messages can be sent with a networking node’s send() (https://docs.auto-pi-lot.com/en/latest/networking/node.html#autopilot.networking.node.Net_Node.send) method, or prepared beforehand by explicitly making a Message (https://docs.auto-pi-lot.com/en/latest/networking/message.html#autopilot.networking.message.Message) and calling its serialize() (https://docs.auto-pi-lot.com/en/latest/networking/message.html) method.

Autopilot’s efficient design lets it access the best of both worlds—the speed and responsiveness of compiled code on dedicated microprocessors and the accessibility and flexibility of interpreted code.

### 2.2 Flexibility

Single-language

Behavior software that uses dedicated microprocessors must have some routine for compiling the high-level abstraction of the experiment into machine code. This gives those systems a theoretical advantage in processing speed, but the compiler becomes the bottleneck of complexity: only those things that can be compiled can be included in the experiment. This may in part contribute to the ubiquity of statemachine formalisms in behavior software.
Because Python is used throughout the system, extending Autopilot’s functionality is straightforward. Task design (see section 3.3) is effectively arbitrary—anything that can be expressed in Python is a valid task. This also allows Autopilot to easily be extended to make use of external libraries (eg. our integration with DeepLabCut-Live[25] and our planned integration with OpenEphys).

Modularity

Although Autopilot deeply integrates with the Raspberry Pi’s hardware, we have also worked to make its components modular. There is a tension between providing a full-featured behavioral system and the flexibility of its components — as additional features are added to a system, they can constrain the functionality of existing components that they rely on. To address this tension, we have continuously worked to decouple Autopilot into subcomponents with clear inheritance hierarchies and APIs that can used quasi-independently.
Modularity has 3 primary advantages:
1. Modularity makes code more flexible by reducing the constraints imposed by
unstructured code interdependencies | ._.
2. Modularity makes code more intelligible by logically distributing tasks to
discrete classes | ._. *-* | ^ ^ =.=
3. Modularity reduces effort-duplication by allowing multiple, similar classes
._. | ._. | ._. | ._. to be created with inheritance rather than copying and pasting.

14 autopilot automating behavioral experiments with lots of raspberry pis

There is no such thing as “incompatible hardware”withAutopilot because the classes
that control hardware are independent from the code that provides other core functionality. In systems without modular design, hardware implementation is spread across the codebase; for example to add a new type of hardware output to a Bpod system, one would need to write new firmware for it in C, (https://github.com/sanworks/Bpod_Gen2/blob/master/FIRMWARE%20README.txt) modify Bpod’s existing firmware, (https://github.com/sanworks/Bpod_StateMachine_Firmware/blob/v22/Preconfigured/StateMachine-Bpod2_0/StateMachine-Bpod2_0.ino) hunt through the code to modify howstates are added (https://github.com/sanworks/Bpod_Gen2/blob/71f3a256b68926b65eae71e10fd747bd28e7ba7d/Functions/State%20Machine%20Assembler/AddState.m) and state machines are assembled, (https://github.com/sanworks/Bpod_Gen2/blob/71f3a256b68926b65eae71e10fd747bd28e7ba7d/Functions/%40BpodObject/SetupStateMachine.m) add its controls explicitly to the GUI, (https://github.com/sanworks/Bpod_Gen2/blob/71f3a256b68926b65eae71e10fd747bd28e7ba7d/Functions/Override%20Panels/StateMachinePanel_2_0_0.m) and so on.
Tasks specify what type of hardware is needed to run them, but are agnostic about theway the hardware is implemented, making their descriptions more portable. Tasks that have the same structure but differ in hardware (eg. a freely moving two-alternative forced choice task in which a mouse visits several IR sensors, or a head-fixed two-alternative forced choice task in which a mouse runs on a wheel to indicate its choice) can be implemented by a trivial subclass that modifies the hardware description rather than completely rewriting the task.

Plugins & Code Transparency

We call Autopilot a software framework because in addition to providing classes and methods to run experiments out of the box, it also provides explicit structure that scaffolds any additional code that is needed by the user. Our goal is to clearly articulate in the documentation how modules should interact so that anyone can write code that works on any apparatus.
As groupware intended to be used differently by lab members with different responsibilities, Autopilot is designed for users with a range of programming expertise, from those who only want to interact with a GUI, to those who wish to fundamentally rewrite core operations for their particular experiment. As such, it is extensively documented: this paper provides a high-level introduction to its design and structure, its user guide describes how to use the program and provides examples, and
its API-level documentation describes in granular detail how the program actually
works⁴
. Nothing is “off-limits” to the user—there isn’t any hidden, undocumented 4 The user guide and API documentation are available at docs.auto-pi-lot.com (https://www.biorxiv.org/content/10.1101/807693v1docs.auto-pi-lot.com) hardware code behind the curtain. We want users to be able to understand how
and why everything works the way it does so that Autopilot can be adapted and
expanded to any use-case.
A broader goal of Autopilot is to build a library of flexible task prototypes that can
be tweaked and adapted, hopefully reducing the number of times the wheel is reinvented. We have attempted to nudge users to write reusable tasks by designing Autopilot such that rather than writing tasks as local unstructured scripts, they use its plugin system that scaffolds development by extending any of its basic types. Plugins are registered using a form in the Autopilot Wiki which makes them available to anyone (https://wiki.auto-pi-lot.com/index.php/Autopilot_Plugins) while also embedding them in a semantically annotated information system that allows giving explicit credit to contributors, programmatically linking to any
derivative publications that use the plugin, and further documentation of any tasks,
hardware, or other extensions included within the plugin. Inheriting from parent
classes give plugins structure and a set of basic features⁵ while also being maximally 5 Like inheriting from the GPIO (https://docs.auto-pi-lot.com/en/latest/hardware/gpio.html#autopilot.hardware.gpio.GPIO) class gives GPIO
plugins a systematic means of interacting with the underlying pigpiod daemon.

permissive — anything can be overridden and modified.

design 15

Message Handling

Modular software needs a well-defined protocol to communicate between modules, andAutopilot’s is heavily influenced by the concurrency philosophy⁶ of ZeroMQ[20]. ⁶
“ZeroMQ [...] has a subversive effect on how you develop network-capable applications. [...] message processing rapidly becomes the central loop, and your application soon breaks down into a set of message processing tasks.”
“If there’s one lesson we’ve learned from 30+ years of concurrent programming, it is: just don’t share state.”
-The ZeroMQ Guide (http://zguide.zeromq.org/)

All communication between computers and modules happens with ZeroMQ messages, and handling those messages is the main way that Autopilot handles events. A key design principle is that Autopilot components should not “share state”—they can communicate, but they are not dependent on one another. While this may seem like a trivial detail, having networking and message-handling at its core has three advantages that make Autopilot a fundamental departure from previous behavioral software.
First, new software modules can be added to any system by simply dropping in a standalone networking object. There is no need to dramatically reorganize existing code to make room for new functionality. Instead new modules can receive, process, and send information by just connecting to a parent module in the swarm. For example, each plot opens a network connection to stream incoming task data independently from the stream that is saving the data.
Second, Autopilot can be made to interact with other software libraries that use ZeroMQ. For example, The OpenEphys GUI for electrophysiology can send and receive ZMQ messages (https://open-ephys.atlassian.net/wiki/spaces/OEW/pages/23265310/Network+Events) to execute actions such as starting or stopping recordings. Interaction with other software is also useful in the case that some expensive computation needs to happen mid-task. For example, one could send frames captured from a video camera on a Raspberry Pi to a GPU computing cluster for tracking the position of the animal. Since ZeroMQ messages are just TCP packets it is also possible to communicate over the internet for remote control or to communicate with a data server.
Third, making every component network-capable allows tasks to be distributed over multiple Raspberry Pis. Chaining multiple Pis distributes the computational load, allowing, for example, one Raspberry Pi to record and process video while another runs a sound server and delivers rewards. Autopilot expands with the complexity of your task, simultaneously eliminating limitations on quantity of hardware peripherals while ensuring latency is minimal. More interestingly, distributing tasks allows the arbitrary construction of what we call “behavioral topologies,” which we describe in section 3.7.

### 2.3 Reproducibility

We take a broad view on reproducibility: including not only the ability to share data and recreate experiments, but also integrating into a broader ecosystem of tools that reduces labor duplication and encourages sharing and organizing technical knowledge. For us, reproducibility means building a set of tools that make every experiment and every technique available to anyone, anywhere.

Standardized task descriptions

0.00

0.25

0.50

0.75

1.00

4 | 6 | 8
Reward Volume (uL)

Successful Mice

Figure 2.4: “Minor” details have major effects. Proportion of mice (each point, n=4) that were successful learning the first stage of the speech task described in [45] across 10 behavior boxes with variable reward sizes. A 2µL difference in reward size had a surprisingly large effect on success rate.

The implementation and fine details of a behavioral experiment matter. Seemingly trivial details like milliseconds of delay between trial phases and microliters of reward volume can be the difference between a successful and unsuccessful task (Fig-

16 autopilot automating behavioral experiments with lots of raspberry pis

ure 2.4). Reporting those details can thus be the difference between a reproducible
and unreproducible result. Researchers also often use “auxiliary” logic in tasks—
such as methods for correcting response bias—that are never completely neutral to the interpretation of results. These too can be easily omitted due to brevity or memory in plain-English descriptions of a task, such as those found in Methods sections. Even if all details of an experiment were faithfully reported, the balkanization of behavioral software into systems peculiar to each lab (or even to individuals within a lab) makes actually performing a replication of a behavior result expensive and technically challenging. Widespread use of experimental tools that are not explicitly designed to preserve every detail of their operation presents a formidable barrier to rigorous and reproducible science[53].

{
"step_name" | : | "tone_discrim",
"task_type" | : | "2AFC",
"bias_mode" | : 0,
"punish_sound" : false,
"stim" : {
"sounds" : {
"L": {
"duration" : 100,
"frequency" : 10000,
"type" | : | "tone",
"amplitude" : 0.01},
"R": {"...":"..."}}},
"reward": {
"type" | : | "volume",
"volume" | : 20},
"graduation" : {
"type" | : | "accuracy",
"threshold" : 0.75,
"window" : 400},
}
Figure 2.5: Task parameters are stored as portable JSON, formatting has been abbreviated for clarity.

Autopilot splits experiments into a) the code that runs the experiment, which is intended to be standardized and shared across implementations, and b) the parameters (Figure 2.5) that define your particular experiment and system configuration. For example, two-alternative forced choice tasks have a shared structure regardless of the stimulus modality, but only your task plays pitch-shifted national anthems. This division of labor, combined with Autopilot’s structured plugin system, help avoid the ubiquitous problem of rig-specific code and hard-coded variables making experimental code only useful on the single rig it was designed for: enabling the possibility of a shared library of tasks as described in section 2.2
The practice of reporting exactly the parameter description used by the software to run the experiment removes any chance for incompleteness in reporting. Because all task parameters are included in the produced data files, tasks are fully portable and can be reimplemented exactly by anyone that has comparable hardware to yours.

Self-Documenting Data

A major goal of the open science movement is to normalize publishingwell-documented and clearly-formatted data alongside every paper. Typically, data are acquired and stored in formats that are lab-idiosyncratic or ad-hoc, which, over time, sprout entire software libraries needed just to clean and analyze it. Idiosyncratic data formats hinder collaboration within and between labs as the same cleaning and analysis operations gain multiple, mututally incompatible implementations, duplicating labor and multiplying opportunities for difficult to diagnose bugs. Over time these data formats and their associated analysis libraries can mutate and become incompatible with prior versions, rendering years of work inaccessible or uninterpretable. In one worst-case scenario, the cleaning process unearths some critically missing information about the experiment, requiring awkward caveats in the Methods section or months of extra work redoing it. In another, the missing information or bugs in analysis code are never discovered, polluting scientific literature with inaccuracies. The best way to make data publishable is to avoid cleaning data altogether and design good data hygiene practices into the data acquisition process. Autopilot automatically stores all the information required to fully reconstruct an experiment, including any changes in task parameters or code version that happen throughout training as the task is refined.

root
current_task
data
task_name
S00_free_water
trial_data
S01_tone_discrim
trial_data
history
git_hashes
parameter_history
past_protocols
old_task
weights
info
animal_id
birth_date
genotype
etc_additional_info
Figure 2.6: Example data structure. All information necessary to reconstruct an experiment is automatically stored in a human-readable HDF5 file.

Autopilot data is stored in HDF5 (https://support.hdfgroup.org/HDF5/whatishdf5.html) files, a hierarchical, high-performance file format. HDF5 files support metadata throughout the file hierarchy, allowing annotations to natively accompany data. Because HDF5 files can store nearly all commonly used

design 17

data types, data from all collection modalities—trialwise behavioral data, continuous electrophysiological data, imaging data, etc.—can be stored together from the time of its acquisition. Data is always stored with the full conditions of its collection, and is ready to analyze and publish immediately (Figure 2.6). No Autopilot-specific scripts are needed to import data into your analysis tool of choice—anything that can read HDF5 files can read Autopilot data⁷
7 Though our Subject class provides a simplified interface to access and manipulate Autopilot data
As of v0.5.0, we have built a formal data modeling system into Autopilot, allowing for unified declaration of data for experimental subjects, task parameters, and resulting data with verifiable typing and human-readable annotations. These abstract data models can be used with multiple storage interfaces, allowing export to, for example, the Neurodata Without Borders standard[42], further enabling Autopilot data to be immediately incorporated into existing processing pipelines (see section 3.2).

Testing & Continuous Integration

Open-source scientific software explodes prior limitations to access and inspection imposed by proprietary tools. It also exposes the research process to bugs in software written by semi-amateurs that can yield errors in the resulting data, analysis, and interpretation[48, 15, 8, 34]. Autopilot tries to bring best practices in software development to experimental software, including a set of automated tests for continuous integration.
We are still formalizing our contribution process, and our tests are still far from achieving full coverage⁸
, but we currently require tests and documentation for all 8 Coverage statistics for Autopilot are available on
coveralls.io at https://coveralls.io/github/wehr-lab/autopilot (https://coveralls.io/github/wehr-lab/autopilot)

new code added to the library. Writing good tests is hard, and we are in the process of building a set of hardware simulators and test fixtures to ease contribution. Tests are effectively provable statements about how a program functions (Figure 2.7), which are particularly important for a library that aspires to be baseline lab infrastructure like Autopilot. Tests make it possible to use and contribute to the library with confidence: all tests are run on every commit, making it possible to determine if some new contribution breaks existing code without manually reading and testing every line. As we work to complete our test coverage, we hope to provide researchers with a tool that they can trust and elevates the verifiability of scientific results at large.

def test_set_gpio():
"""
The `set` method of a Digital_Out object sets the pin state
"""
pin = Digital_Out(pin=17)

# Turn GPIO pin on

pin.set(True)
assert pin.state == True

# Turn GPIO pin off

pin.set(False)
assert pin.state == False
Figure 2.7: A test like test_set_gpio is a provable statement about the functionality of a program, in this case that “the Digital_Out.set() method sets the state of a GPIO pin.”

Expense

Autopilot is an order of magnitude less expensive than comparable behavioral systems (Table 2.3). We think the expense of a system is important for two reasons: scientific equity and statistical power.
The distribution of scientific funding is highly skewed, with a large proportion of research funding concentrated in relatively few labs[26]. Lower research costs benefit all scientists, but lower instrumentation costs directly increase the accessibility of state-of-the-art experiments to labs with less funding. Since well-funded labs also tend to be concentrated at a few (well-funded) institutions, lower research costs also broaden the base of scientists outside traditional research institutions that can stay at the cutting edge[5, 13, 39].

0.50

0.75

1.00
Positi

ves

ICC | 0.0002 | 0.002
| 0.02 | 0.2

α = .05

18 autopilot automating behavioral experiments with lots of raspberry pis

Neuroscience also stands to benefit from the lessons learned from the replication
crisis in Psychology[46]. In neuroscience, underpowered experiments are the rule,
rather than the exception[10]. Statistical power in neuroscience is arguably even worse than it appears, because large numbers of observations (eg. neural recordings) from a small number of animals are typically pooled, ignoring the nested structure of observations collected within individual animals. Increasing the number of cells recorded from a small number of animals dramatically increases the likelihood of Type I errors (Figure 2.8)—indeed, for values of within-animal correlation typical of neuroscientific data, high numbers of observations make Type I errors more likely than not[1]. For this reason, perhaps paradoxically, recent technical advances in multiphoton imaging and silicon-probe recordings will actually make statistical rigor in neuroscience worse if we don’t use analyses that account for the multilevel structure of the data and correspondingly record from the increased number of animals that they require.
Although the expense of multi-photon imaging and high-density electrophysiology will always impose an experimental bottleneck, behavioral training time is often the greater determinant of study sample size. Typical behavioral experiments require daily training sessions often carried out over weeks and months, while far fewer imaging or electrophysiology sessions are carried out per animal. Training large cohorts of animals in parallel is thus the necessary basis of a well-powered imaging or electrophysiology experiment.
| Autopilot | pyControl | Bpod
Behavior CPU | $45 (https://www.adafruit.com/product/4292) | $270 (https://open-ephys.org/pycontrol/pycontrol) | $925 (https://sanworks.io/shop/viewproduct?productID=1024)
Nosepoke (3x) | $216 | $369 (http://www.open-ephys.org/store/pycontrol-peripherals) | $810 (https://sanworks.io/shop/viewproduct?productID=1009)
Total for One | $261 | $639 | $1735
Five Systems | $1305 | $3195 | $8675
Host CPU(s) | $1000 | $1000 | $5000
Total for Five | $2305 | $4195 | $13625
Total for Ten | $3610 | $8390 | $27350

Table 2.3: Cost for Basic 2AFC System “Nosepoke” includes a solenoid valve, IR sensor, water tube, LED, housing, and any necessary driver PCBs. For PyControl and Autopilot, we included the cost of one Lee LHDA0531115H (https://wiki.auto-pi-lot.com/index.php/Lee_LHDA0531115H) solenoid valve per nosepoke ($63.35). For PyControl, we estimated a typical USB hub with 5 ports to control 5 pyControl systems from one computer. We note that the Bpod and PyControl systems both include cost of assembly for the control CPUs and nosepokes, but also that Autopilot does not require assembly for its control CPU and its default nosepoke is a snap-together 3D printed part and PCB without surface mounted components that can be assembled by an amateur in roughly half an hour.

3

# Program Structure

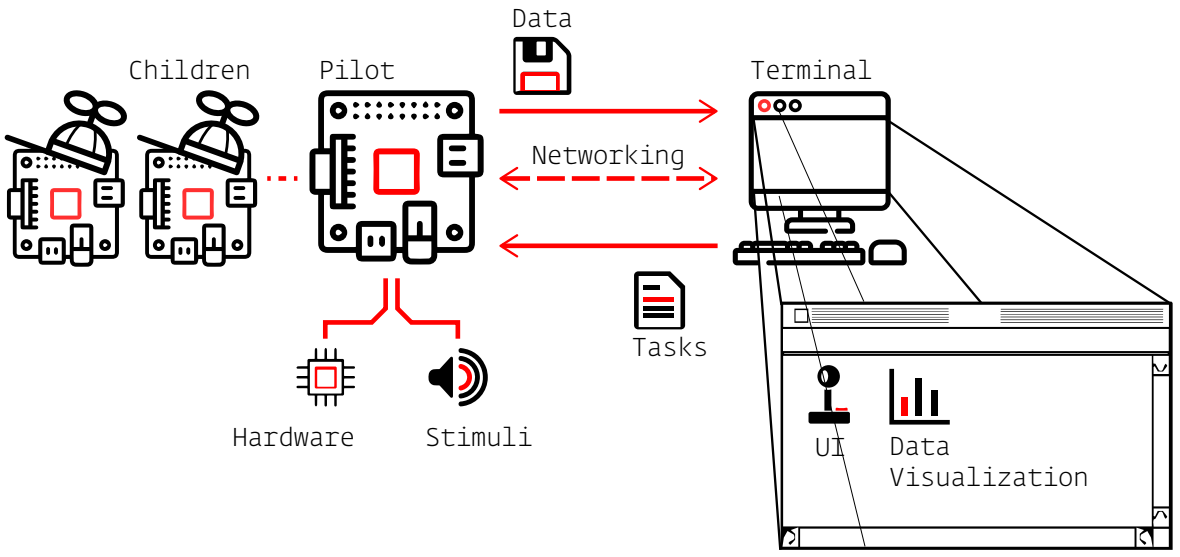
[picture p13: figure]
Hardware; Stimuli; Tasks; Data; Data Visualization; Pilot; Terminal; Networking; Children

Figure 3.1: Overview of major Autopilot components
Autopilot consists of software and hardware modules that are configured to create a behavioraltopology. Independentagentslinked by flexible networking objects fill different roles within a topology, such as hosting the user interface, controlling hardware, or delivering stimuli. This infrastructure is ultimately organized to perform a behavioral task.

### 3.1 Directory Structure

On setup, Autopilot creates a user directory that contains all local files that define its operation (Figure 3.2). The subdirectories include:

./autopilot
├── calibration
├── data
│ ├── subject_1.h5
│ └── subject_2.h5
├── launch_autopilot.sh
├── logs
│ ├── core.terminal.log
│ └── plugins.my_plugin.log ├── pilot_db.json
├── plugins
│ └── my_plugin
│ | └── my_task.py
├── prefs.json
├── protocols
│ ├── 2afc_easy.json
│ └── 2afc_hard.json
└── sounds
Figure 3.2: Example user directory structure, typically in ∼/autopilot.
- calibration — Calibration for hardware objects like audio or solenoids that, for example, map opening durations to volumes of liquids dispensed
- data — Data for experimental subjects
- launch_autopilot.sh — Launch script that includes launching external processed like the jack audio daemon (will be removed and integrated into a more formal agent structure in future versions)
- logs — Every Autopilot object is capable of full debug logging, neatly formatted by object type and instance ID and grouped within module-level logging files.

20 autopilot automating behavioral experiments with lots of raspberry pis

Logs are both written to disk, and output to stderr using the rich logging handler (https://rich.readthedocs.io/en/latest/reference/logging.html#logging) for clean and readable inspection during program operation (Figure 3.3).
Logs can be parsed back into python objects to make it straightforward to diagnose problems or recover data in the case of an error.

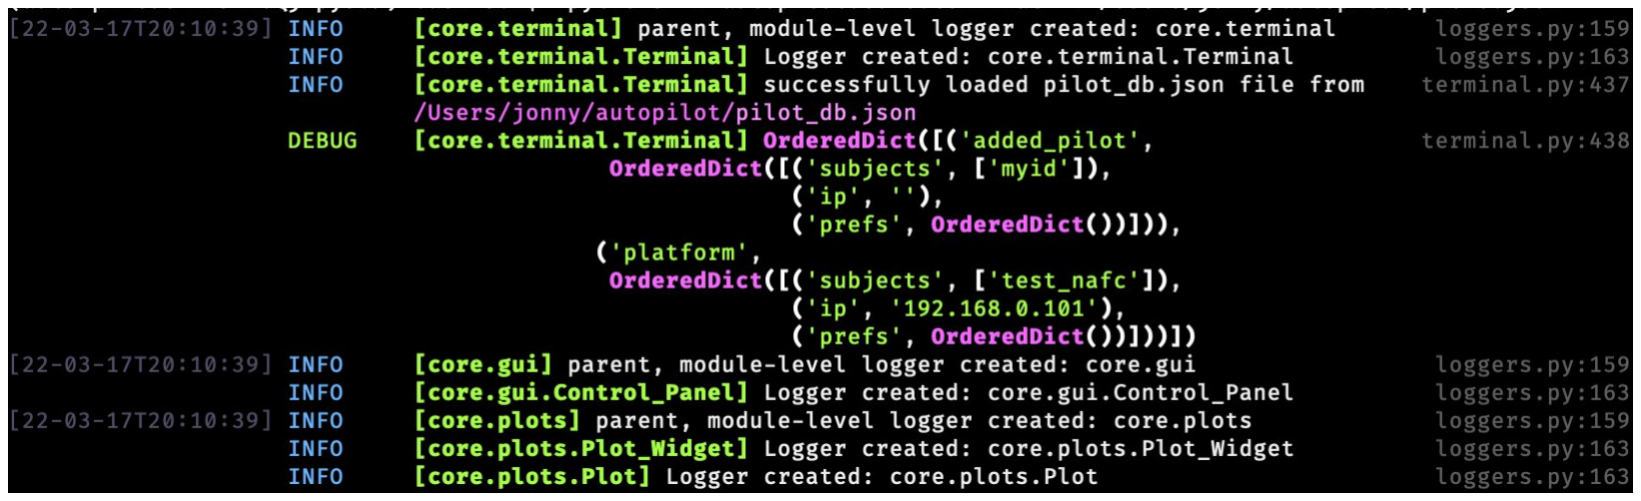
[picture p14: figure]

Figure 3.3: Logs printed to stderr are formatted and colorized by the rich logging handler (https://rich.readthedocs.io/en/latest/reference/logging.html#logging)
- pilot_db.json — A .json file that stores information about associated Pilots, including the contents of their prefs files, which hash/version of Autopilot they are running, and any Subjects that are associated with them.
- plugins — Plugins, which are any Python files that contain subclasses of Autopilot objects, that are automatically made available by Autopilot’s registry (https://docs.auto-pi-lot.com/en/latest/utils/registry.html) sys-
tem (eg. autopilot.get('hardware', 'My_Hardware') would retrieve a cus-
tom hardware object). Plugins can be documented and made available to other Autopilot users by registering them on the wiki (https://wiki.auto-pi-lot.com/index.php/Autopilot_Plugins)
- prefs.json — Configuration options for this particular Autopilot instance, including configurations of local hardware objects, audio output, etc. In the future this will likely be broken into multiple files for different kinds of preferences¹
1 with care for backwards compatibility
- protocols — Protocols, which consist of parameterizations of individual Tasks as well as criteria for graduating betwewen them. These are also stored in individual subject data files, and updated whenever the source protocol files change.
- sounds — Any sound files that are requested by the File (https://docs.auto-pi-lot.com/en/latest/stim/sound/sounds.html#autopilot.stim.sound.sounds.File) sound class.

### 3.2 Data

As of v0.5.0, Autopilot uses pydantic (https://pydantic-docs.helpmanual.io/) to create explicitly typed and schematized data models. Submodules include data abstract modeling tools that define base model types like Tables, Groups, and sets of Attributes. These base modeling classes are then built into a few core data models like subject Biography information, Protocol declaration, and the Subject data model itself that combines them. Modeling classes then have multiple interfaces that can be used to create equivalent objects in other formats, like pytables for hdf5 storage, pandas dataframes for analysis, or exported to Neurodata Without Borders.
For example, consider a simplified version of the Biograpphy model:

program structure 21

data - Biography
1 | from autopilot.data.modeling import Data, Attributes
2 | from typing import Optional, Union

3
4 | class Enclosure(Data):
5 | """Where does the subject live?"""
6 | box: Optional[Union[str, int]] = Field(
7 | default=None,
8 | description="The box this Subject lives in"
9 | )
10 | room: Optional[Union[str, int]] = Field(
11 | default=None,
12 | description="The room number that the animal is housed in"
13 | )

14
15 | class Biography(Attributes):
16 | """Biography of an Experimental Subject"""
17 | id: str = Field(...
18 | description="The indentifying name of this subject."
19 | )
20 | dob: datetime = Field(...
21 | description="The Subject's date of birth"
22 | )
23 | enclosure: Optional[Enclosure] = None

24
25 | @property
26 | def age(self) -> timedelta:
27 | """Difference between now and :attr:`.dob`"""
28 | return datetime.now() - self.dob

A new subject could then be created with this biography like this, storing it in the HDF5 file and returning an exact copy when requested:

| data - New Subject
1 | from autopilot.data import Subject

2
3 | bio = Biography(
4 | id="my_subject",
5 | dob="2022-01-01T00:00:00",
6 | enclosure=Enclosure(box=100, room="Building 200")
7 | )
8 | sub = Subject.new(bio)
9 | assert sub.info == bio

The models are declared using a combination of python type hints²
and Field ob- 2 Python type hints (https://docs.python.org/3/library/typing.html) are colon delimited annotations like this: x:int = 1 that indicate the type (integer, string, etc.) of the variable. Though typically Python does not, Pydantic both validates that a type matches its hint and coerces it to the correct type if possible.

jects that provide defaults and descriptions. Because these models can be recursive, as in the case of using the Enclosure model as a type within the Biography model, we can build expressive, flexible, but still strict representations of complex data. Out of the box, pydantic models can create explicit and interoperable schemas (https://pydantic-docs.helpmanual.io/usage/schema/) in

22 autopilot automating behavioral experiments with lots of raspberry pis

JSON Schemaand (https://json-schema.org/draft/2020-12/json-schema-core.html) OpenAPI (https://github.com/OAI/OpenAPI-Specification) formats, and Autopilot extends them with additional
interfaces and representations. Autopilot can create a GUI form for filling in fields
for models, for example, to create a new Subject or declare parameters for a task (Figure 3.2). Attribute models that consist of scalar key-value pairs can be reliably stored and retrieved from metadata attribute sets in HDF5 groups, but Autopilot knows that Table models should be created as HDF5 tables as they will have multiple values for each field. An additional Trial_Data class that inherits from Table can be exported to NWB trial data, and the Subject.get_trial_data method uses the model to load trial data and convert it to a correctly typed pandas[32] DataFrame.

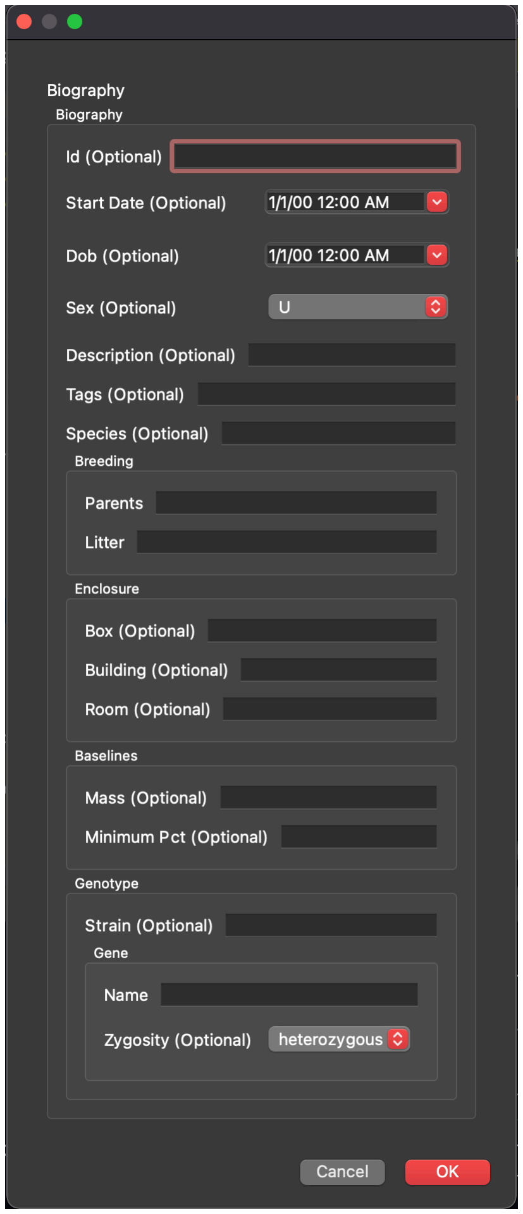
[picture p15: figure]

Figure 3.4: An Autopilot Data model can automatically generate a GUI form to fill in its properties, in this example to define a new experimental Subject’s biography.

Though the data modeling system is new³
, we have laid the groundwork for Au-

3 Released as an alpha version at the time of writing topilot’s plugin system to allow researchers to declare custom schema for all data produced by Autopilot, and to preserve both interoperability and reproducibility by combining them with datasets potentially produced by multiple incompatible tools (see 5).

### 3.3 Tasks

task_0

stages

protocol

graduation
task_1

Figure 3.5: Protocols consist of one or multiple tasks, tasks consist of one or multiple stages. Completion of all of a task’s stages constitutes a trial, and meeting some graduation criterion like accuracy progresses a subject between tasks.

Behavioral experiments in Autopilot are centered around tasks. Tasks are Python classes that describe the parameters, coordinate the hardware, and perform the logic of the experiment. Tasks may consist of one or multiple stages, completion of which constitutes a trial (Figure 3.5). Stages are analogous to states in the finite state machine formalism.
Multiple tasks are combined to make protocols, in which animals move between tasks according to “graduation” criteria like accuracy or number of trials. Training an animal to perform a task typically requires some period of shaping where they are familiarized to the apparatus and the structure of the task. For example, to teach animals about the availability of water from “nosepoke” sensors, we typically begin with a “free water” task that simply gives them water for poking their nose in them. Having a structured protocol system prevents shaping from relying on intuition or ad hoc criteria.

Task Components

The following is a basic two-alternative choice (2AFC) task—a sound is played and an animal is rewarded for poking its nose in a designated target nosepoke. While simple, it is included here in full to show how one can program a task, including an explicit data and plotting structure, in roughly 60 lines of generously spaced Python.

program structure 23

Every task begins by describing four elements:
1) the task’s parameters, 2) the data that will be collected, 3) how to plot the data, and 4) the hardware that is needed to run the task.

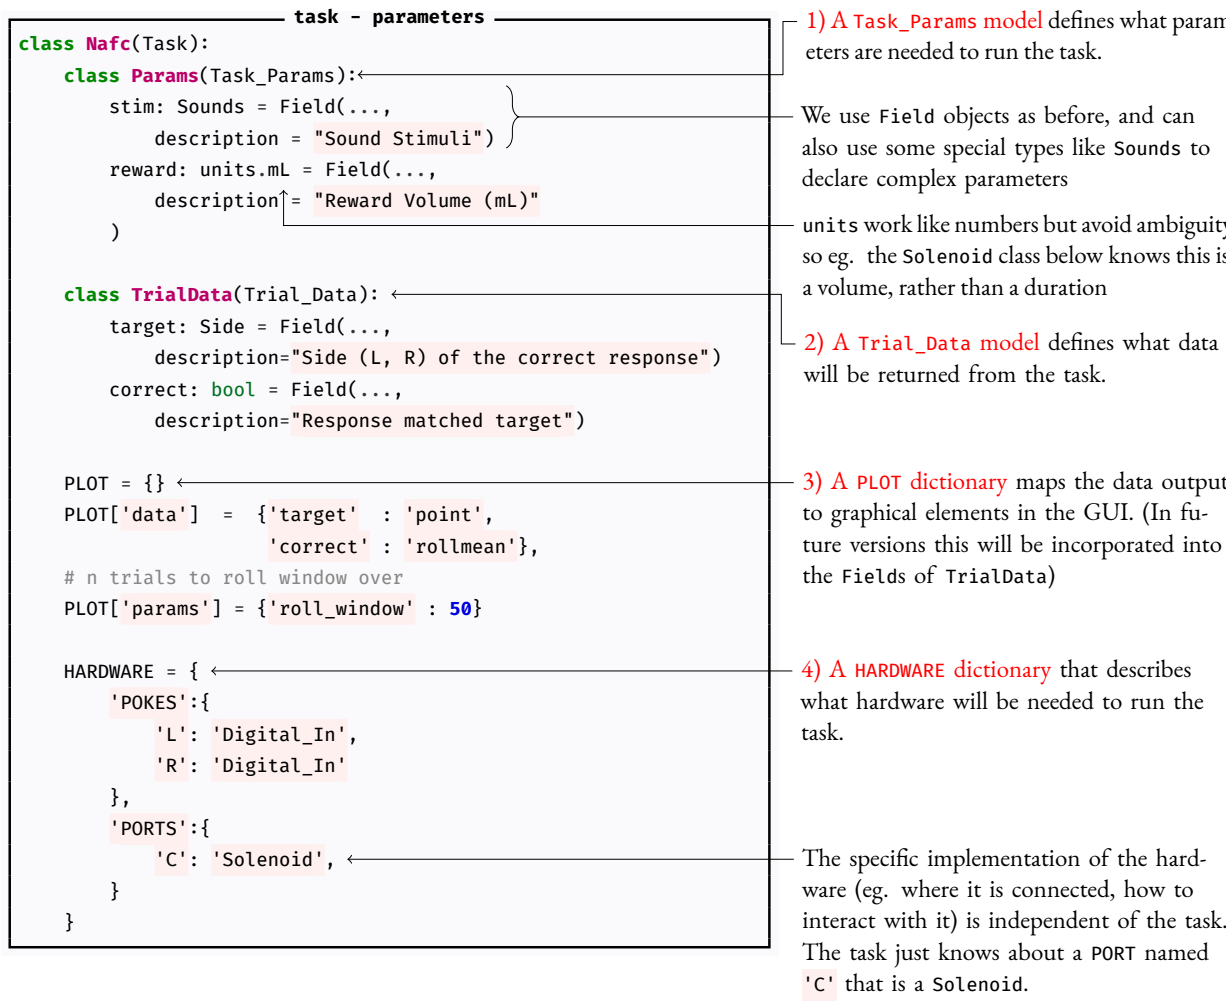
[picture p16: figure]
task - parameters; class Nafc(Task): class Params(Task_Params): stim: Sounds = Field(..., description = "Sound Stimuli") reward: units.mL = Field(..., description = "Reward Volume (mL)"; class TrialData(Trial_Data): target: Side = Field(...,; correct: bool = Field(..., description="Response matched target"); PLOT = {} PLOT['data'] = {'target' : 'point', 'correct' : 'rollmean'}, # n trials to roll window over PLOT['params'] = {'roll_window' : 50}; HARDWARE = { 'POKES':{ 'L': 'Digital_In', 'R': 'Digital_In'; }, 'PORTS':{ 'C': 'Solenoid',; eters are needed to run the task.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

description="Side (L, R) of the correct response")

1) A Task_Params model defines what param-

also use some special types like Sounds to

units work like numbers but avoid ambiguity, so eg. the Solenoid class below knows this is

3) A PLOT dictionary maps the data output to graphical elements in the GUI. (In future versions this will be incorporated into

The specific implementation of the hard-

interact with it) is independent of the task.

Created tasks receive some common methods, like input/trigger handling and networking, from an inherited metaclass. Python inheritance can also be used to make
small alterations to existing tasks⁴
rather than rewriting the whole thing. The GUI 4 An example of subclassing a generic ’Task’ class is
will use the | included in Autopilot’s user guide (http://docs.auto-pi-lot.com/guide.task.html) Params model and the PLOT dictionary to generate forms for parameter-
izing the task within a protocol and display the data as it is collected. The Subject
class will use the TrialData model to create HDF5 tables to store the data, and the
Task metaclass will instantiate the described HARDWARE objects from their systemspecific configuration in the prefs.json file so they are available in the rest of the
class like self.hardware['POKES']['L'].state

24 autopilot automating behavioral experiments with lots of raspberry pis

Stage Methods

The logic of tasks is described in one or a series of methods (stages). The order of stages can be cyclical, as in this example, or can have arbitrary logic governing the transition between stages.

task - methods
def __init__(self, params:'Nafc.Params'): self.stim_mgr = Stim_Manager(params.stim)
32 | self.reward | = Reward_Manager(params.reward)

stage_list = [self.discrim, self.reinforcement] self.stages = itertools.cycle(stage_list)

self.init_hardware()
next(self.stages)()
| def discrim(self):
target, wrong, stim = self.stim_mgr.next() self.target = target

self.triggers[target] = [
self.hardware['PORTS']['C'].open,
lambda: next(self.stages)()] self.triggers[wrong] = lambda: next(self.stages)()

self.node.send('DATA', {'target':target})

| stim.play()

def reinforcement(self, response):
if response == self.target: self.node.send('DATA', {'correct':True})
| else:
self.node.send('DATA', {'correct':False})

next(self.stages)()

In Python, def defines new methods. The __init__ method is called when a new object is initialized
Managers control stimulus and reward delivery, so users can, for example, continually synthesize new stimuli or implement adaptive rewards
Stages are combined into an object that (in this case) continually cycles through them when its next() method is called.
This starts the task by retrieving the first stage and then calling it.

The stimulus manager returns which port will be the target and the sound to be played.
A sequence of triggers is set: if the target port is poked, a reward will be delivered and the next stage will be called. A lambda function indicates not to call the method now, but only when triggered.
The task has a networking object that asynchronously streams data back to the user-facing terminal
In this example, the response port is passed from the trigger handling function. If it matches the stored target variable, the animal answered correctly.

Finally, the task is repeated by calling the next stage.

Autopilot is not prescriptive about how tasks are written. The same task could have two separate methods for correct and incorrect answers rather than a single reinforcement method, or only a single stage that blocks the program while it waits for a response.

{
"step_name": "Simple 2AFC", "stim" : {
"sounds" : {
"L": {
"type" | : "tone",
"frequency" : 4000},
"R": {
"type" | : "tone",
"frequency" : 8000}
}
},
"reward": 10
}
Figure 3.6: Simplified example of parameters for the above task

Publishing data from this task requires no additional effort: a hash that uniquely identifies the code version (as well as any local changes) is automatically stored at the time of collection, as is a JSON-serialized version of the parameter model (Figure 3.6). If this task was incorporated into the central task library, anyone using Autopilot would be able to exactly replicate the experiment from the published data.

program structure 25

The limitations of finite state machines

The 2AFC task described above could be easily implemented in a finite-state machine. However, the difficulty of programming a finite-state machine is subject to combinatoric explosion with more complex tasks. Specifically, finite-state machines can’t handle any task that requires any notion of “state history.”
As an example, consider a maze-based task. In this task, the animal has to learn a particular route through a maze—it is not enough to reach the endpoint, but the animal has to follow a specific path to reach it (Figure 3.7). The arena is equipped with an actimeter that detects when the animal enters each area.
a | b | c
d | e | f
g | h | i

good! reward!

bad. no reward :(

Figure 3.7: The subject must reach point i but only via the correct (green) path.

In Autopilot, we would define a hardware object that logs positions from the actimeter with a store_position() method. If the animal has entered the target position (“i” in this example), a task_trigger() that advances the task stage is called. The following code is incomplete, but illustrates the principle.

maze - hardware
1 | class Actimeter(Hardware):
2 | def __init__(self):
3 | # ... some code to access the hardware ...
4 | self.positions = []
5 | self.target_position = "i"

6
7 | def store_position(self, position):
8 | self.positions.append(position)

9
10 | if position == self.target_position:
11 | self.finished_cb(self.positions)
12 | self.positions = []

See line 18 below

The task follows, with parameters and network methods for sending data omitted for clarity.

maze - task
13 | class Maze(Task):
14 | def __init__(self):
15 | self.target_path = ['a', 'b', 'e', 'f', 'i']

16
17 | self.actimeter = Actimeter()
18 | self.actimeter.finished_cb = self.finished

19
20 | def finished(self, positions):
21 | if positions == self.target_path:
22 | self.reward()

The actimeter is given a reference to the Maze task’s finished() method, which it calls when the target position is reached

The sequence of positions is compared to the target_path with ==. If they match, the subject is rewarded!

How would such a task be programmed in a finite-state machine formalism? Since the path matters, each “state” needs to consist of the current position and all the positions before it. But, since the animal can double back and have arbitrarily many state transitions before reaching the target corner, this task is impossible to represent with a finite-state machine, as a full representation would necessitate infinitely many

26 autopilot automating behavioral experiments with lots of raspberry pis

states (this is one example of the pumping lemma, see [27]).
Even if we dramatically simplify the task by 1) assuming the animal never turns back
and visits a space twice, and 2) only considering paths that are less than or equal to the length of the correct path, the finite state machine would be as complex as figure 3.8.
While finite-state machines are relatively easy to implement and work well for simple tasks, they quickly become an impediment to even moderately complex tasks. Even for 2AFC tasks, many desirable features are difficult to implement with a finite state machine, such as: (1) graduation to a more difficult task depending on performance history, (2) adjusting reward volume based on learning rate, (3) selecting or synthesizing upcoming stimuli based on patterns of errors[6], etc.
Some of these problems are avoidable by using extended versions of finite state machines that allow for extra-state logic, but require additional complexity in the code running the state machines to accomodate, and with enough exceptions the clean systematicity that is the primary benefit of finite state machines is lost. Autopilot attempts to avoid these problems by providing toolsto program tasks withoutrequiring a specified format, balancing the increased complexity by scaffolding the broader ecosystem of the experiment like its output data, hardware control, etc. When possible, we have tried to avoid forcing people to change the way they think about their work to fit our “little universe”⁵
and instead try to provide a set of tools that let

5 We take inspiration from Aaron Swartz’ description of another engineering project, the Semantic Web, that became too precious about its formalisms:
“Instead of the “let’s just build something
that works” attitude that made the Web (and the Internet) such a roaring success [...] they formed committees to form working groups to write drafts of ontologies that carefully listed (in 100-page Word documents) all possible things in the universe and the various properties they could have, and they spent hours in Talmudic debates over whether a washing machine was a kitchen appliance or a household cleaning device. [...] And instead of spending time building things, they’ve convinced people interested in these ideas that the first thing we need to do is write standards. (To engineers, this is absurd from the start—standards are things you write after you’ve got something working, not before!)”[49]
researchers decide how they want to use them.

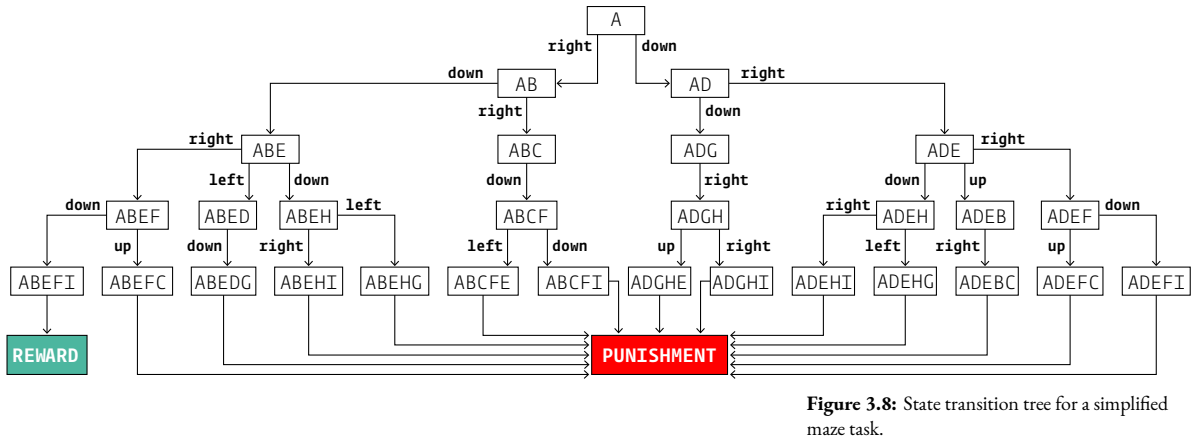
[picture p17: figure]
right; down; left; ABE; ABC; ADG; ADE; ABEF; ABED; ABEH; ABCF; ABCFE; ABCFI; PUNISHMENT; ABEFI; ABEFC; ABEDG; ABEHI; ABEHG; REWARD; ADGH; ADEH; ADEB; ADEF; ADGHE; ADGHI; ADEHI; ADEHG; ADEBC; ADEFC; ADEFI; maze task.

Figure 3.8: State transition tree for a simplified

program structure 27

### 3.4 Hardware

The Raspberry Pi can interface with nearly all common hardware, and has an extensive collection (https://www.raspberrypi.org/help/) of guides, (https://elinux.org/RPi_Guides) tutorials, (https://elinux.org/RPi_Tutorials) and an activeforum (https://www.raspberrypi.org/forums/) to support users implementing new hardware. There is also an enormous amount of existing hardware for the Raspberry Pi, including sound cards, (https://www.hifiberry.com/)motor controllers, (https://www.adafruit.com/product/2348)sensor arrays, (https://www.digikey.com/product-detail/en/raspberry-pi/SENSE-HAT/1690-1013-ND/6196429)ADC/DACs, (https://www.seeedstudio.com/Raspberry-Pi-High-Precision-AD-DA-Board-p-2765.html) and touchscreen displays, (https://www.digikey.com/product-detail/en/pimoroni-ltd/PIM369/1778-1221-ND/9521981) largely eliminating the need for a separate ecosystem of purpose-built hardware (Table 3.1).

Table 3.1: Cost of common peripherals. The native hardware of the Raspberry Pi, low-level hardware control of Autopilot, and availability of inexpensive off-the-shelf components compatible with the raspi make most custom-built peripherals unnecessary.
Device Raspi Bpod
HiFiBerry DAC2 Pro $45 (https://www.hifiberry.com/shop/boards/hifiberry-dac2-pro/) | $445 (https://sanworks.io/shop/viewproduct?productID=1032)
ADC $30 (https://thepihut.com/products/high-precision-adc-hat-for-raspberry-pi-10-channel-32-bit) | $495 (https://sanworks.io/shop/viewproduct?productID=1021)
I2C $0 | $225 (https://sanworks.io/shop/viewproduct?productID=1019)
Ethernet $0 | $285 (https://sanworks.io/shop/viewproduct?productID=1025)
Rotary Encoder $0 | $145 (https://sanworks.io/shop/viewproduct?productID=1022)

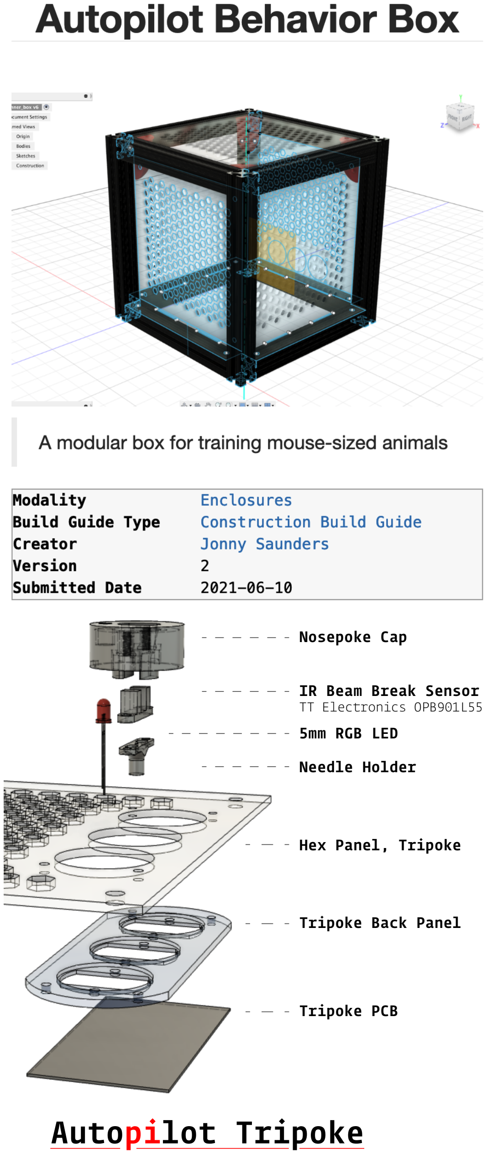
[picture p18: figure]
Nosepoke Cap; IR Beam Break Sensor TT Electronics OPB901L55 5mm RGB LED; Needle Holder; Hex Panel, Tripoke; Tripoke Back Panel; Tripoke PCB; Autopilot Tripoke

Figure 3.9: Two examples of parts with assembly guides available on the autopilot wiki: A modular behavior box (https://wiki.auto-pi-lot.com/index.php/Autopilot_Behavior_Box) with magnetic snap-in panels (top), and a three-nosepoke panel (https://wiki.auto-pi-lot.com/index.php/Autopilot_Tripoke) (bottom).

Autopilot controls hardware with an extensible inheritance hierarchy of Python classes intended to be built into a library of hardware controllers analogously to tasks. Autopilot uses pigpio (http://abyz.me.uk/rpi/pigpio/) to interact with its GPIO pins, giving Autopilot 5µs measurement precision and enabling protocols that require high precision (such as Serial, PWM, and I2C) for nearly all of the pins. Currently, Autopilot also has a family of objects to control cameras (both the Raspberry Pi Cameraand (https://docs.auto-pi-lot.com/en/latest/hardware/cameras.html#autopilot.hardware.cameras.PiCamera) high-speed GENICAM-compliant (https://docs.auto-pi-lot.com/en/latest/hardware/cameras.html) cameras), i2c-basedmotion (https://docs.auto-pi-lot.com/en/latest/hardware/i2c.html#autopilot.hardware.i2c.I2C_9DOF) and heatsensors, (https://docs.auto-pi-lot.com/en/latest/hardware/i2c.html#autopilot.hardware.i2c.MLX90640) andUSB mice. (https://docs.auto-pi-lot.com/en/latest/hardware/usb.html#autopilot.hardware.usb.Wheel) In thefuturewe intend to replace the external pigpio daemon and other performance-critical hardware operations with low-level interfaces written in Rust.
To organize and make available the vast amount of contextual knowledge needed to build and use experimental hardware, we have made a densely linked and publicly editable semantic wiki. (https://wiki.auto-pi-lot.com/index.php/Autopilot_Wiki) The Autopilot wiki contains, among others, reference information for off-the-shelf parts, (https://wiki.auto-pi-lot.com/index.php/Parts) schematics for 2D (https://wiki.auto-pi-lot.com/index.php/2D_CAD) and 3D-printable (https://wiki.auto-pi-lot.com/index.php/3D_CAD) components, and guides (https://wiki.auto-pi-lot.com/index.php/Guides) for building experimental apparatuses and custom parts. The wiki combines unrestrictive freeform editing with structured, computer-readable semantic properties, (https://www.semantic-mediawiki.org/wiki/Semantic_MediaWiki) and we have defined a collection of schemas (https://wiki.auto-pi-lot.com/index.php/Special:CategoryTree?target=Hardware&mode=categories&namespaces=&title=Special%3ACategoryTree) for commonly documented items coupled with submission forms (https://wiki.auto-pi-lot.com/index.php/Special:Forms) for ease of use. For example, the wiki page for the Lee Company solenoid (https://wiki.auto-pi-lot.com/index.php/Lee_LHDA0531115H) we use has fields from a generic Part (https://wiki.auto-pi-lot.com/index.php/Category:Part) schema like a datasheet, price, and voltage, but also that it’s a 3-way, normally-closed solenoid. (https://wiki.auto-pi-lot.com/index.php/Category:Solenoid) The wiki’s blend of structure and freedom breaks apart typically monolithic hardware documentation into a collaborative, multimodal technical knowledge graph. Autopilot can access the wiki through its API, (https://docs.auto-pi-lot.com/en/latest/guide/plugins.html#the-wiki-api) and we intend to tighten their integration over time, including automatic configurations for common parts, usage and longevity benchmarks, detecting mutually incompatible parts, and automatically resolving any additional plugins or dependencies needed to use a part.
Raspberry Pi 4B (https://www.raspberrypi.org/products/raspberry-pi-4-model-b/specifications/) | Teensy 3.6 (https://www.pjrc.com/teensy/techspecs.html) | pyboard (https://micropython.org/)
CPU Clock 1.5GHz | 180MHz | 168MHz
CPU Cores 4 | 1 | 1
Architecture ARMv8-A, 64-bit | ARMv7 32-bit ARMv7 32-bit
RAM Size 2, 4, or 8GB | 256KB | 192KB
Storage MicroSD (any size) | 1024KB | 1024KB
GPU Broadcom VideoCore VI | — | —
GPIO Pins 40 | 58 | 29
USB Ports 2x USB 2.0, 2x USB 3.0 | 2x USB 2.0 | 1x USB 2.0
Ethernet 1Gbps | 100Mbps | —
WiFi 2.4/5 GHz b/g/n/ac | — | —
Camera 15-pin Serial Interface | — | —
Bluetooth | — | —

Table 3.2: Specifications of reviewed behavior hardware. BPod’s state machine uses the Teensy 3.6 microcontroller, and PyControl uses the Micropython Pyboard.

28 autopilot automating behavioral experiments with lots of raspberry pis

### 3.5 Transforms

In v0.3.0, we introduced the transform module, a collection of tools for transforming data. The raw data off a sensor is often not in itself useful for performing an experiment: we want to compare it to some threshold, extract positions of objects in a video feed, and so on. Transforms are like building blocks, each performing some simple operation with a standard object structure, and then composed into a pipeline (Figure 3.10). Pipelines are portable, and can be created on the fly from a JSON representation of their arguments, so it’s easy to offload expensive operations to a more capable machine for distributed realtime experimental control (See [25]).

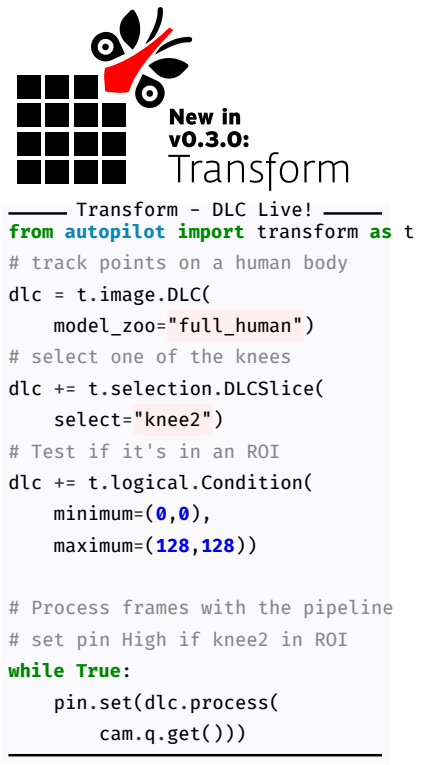
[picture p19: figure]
Transform - DLC Live! from autopilot import transform as t # track points on a human body dlc = t.image.DLC( model_zoo="full_human") # select one of the knees dlc += t.selection.DLCSlice( select="knee2") # Test if it's in an ROI dlc += t.logical.Condition( minimum=(0,0), maximum=(128,128)); # Process frames with the pipeline # set pin High if knee2 in ROI while True: pin.set(dlc.process( cam.q.get()))

Figure 3.10: Transforms can be chained together (here with the in-place addition operator +=) to make pipelines that encapsulate the logical relationship between some input and a desired output. Here pin is a Digital_Out (https://docs.auto-pi-lot.com/en/latest/hardware/gpio.html#autopilot.hardware.gpio.Digital_Out) object, and cam is a PiCamera (https://docs.auto-pi-lot.com/en/latest/hardware/cameras.html#autopilot.hardware.cameras.PiCamera) with queue enabled.

In addition to computing derived values, we use transforms in a few ways, including

- Bridging Hardware — Different hardware devices use different data types, units, scales, so transforms can rescale (https://docs.auto-pi-lot.com/en/latest/transform/units.html#autopilot.transform.units.Rescale) and convert values to make them compatible.
- Integrating External Tools — The number of exciting analytical tools for realtime experiments keep growing, but in practice they can be hard to use together. The transform module gives a scaffolding for writing wrappers around other tools and exposing them to each other in a shared framework, as we did with DeepLabCut-Live[25], making closed-loop pose tracking available to the rest of Autopilot’s ecosystem. We don’t need to rally thousands of independent developers to agree to write their tools in a shared library, instead we want to make wrapping them easy.
- Extending Objects — Transforms can be used to augment existing and create new objects. For example, a motion sensor (https://docs.auto-pi-lot.com/en/latest/hardware/i2c.html#autopilot.hardware.i2c.I2C_9DOF) uses the spheroid (https://docs.auto-pi-lot.com/en/latest/transform/geometry.html#autopilot.transform.geometry.Spheroid) transform to calibrate its accelerometer, and the gammatone filter⁶ (https://docs.auto-pi-lot.com/en/latest/transform/timeseries.html)
extends the Noise (https://docs.auto-pi-lot.com/en/latest/stim/sound/sounds.html#autopilot.stim.sound.sounds.Noise) sound to
6 make a gammatone filtered noise (https://docs.auto-pi-lot.com/en/latest/stim/sound/sounds.html#autopilot.stim.sound.sounds.Gammatone) sound. | a thin wrapper around scipy’s signal.gammatone (https://docs.scipy.org/doc/scipy/reference/generated/scipy.signal.gammatone.html)

Like Tasks and Hardware, the transform module provides a scaffolding for writing
reference implementations of algorithms commonly needed for realtime behavioral
experiments. For example, neuroscientists often want to quickly measure a research
subject’s velocity or orientation, which is possible with inexpensive inertial motion sensors (IMUs), but since anything worth measuring will be swinging the sensor around with wild abandon the readings first need to be rotated back to a geocentric coordinate frame. Since the readings from an accelerometer are noisy, we found a few whitepapers describing using a Kalman filter for fusing the accelerometer and gyroscope data for a more accurate orientation estimate ([2, 38]), but couldn’t find an implementation — so we wrote one. (https://docs.auto-pi-lot.com/en/latest/_modules/autopilot/transform/geometry.html#IMU_Orientation) We integrated it into the IMU class (Figure
3.11) and since it’s an independent transform, it’s available to anyone even if they use nothing else from Autopilot.

Geocentric Velocity
# rotate input in x and y

# by some pitch and roll

reorient = t.geometry.Rotate( dims='xy')
# select the z axis

reorient += t.selection.Slice( select=2)
# remove gravity

reorient += t.math.Add(
-9.8)

# using I2C_9DOF...

angle = imu.rotation
z_accel = reorient.process( imu._acceleration, angle)

Figure 3.11: Using the IMU_Orientation (https://docs.auto-pi-lot.com/en/latest/_modules/autopilot/transform/geometry.html#IMU_Orientation) transform built into the IMU’s rotation property, a processing chain to reorient the accelerometer reading and subtract gravity for geocentric z-axis acceleration.

Transformswere made to be composed, sowe broke it into independent sub-operations: AKalman (https://docs.auto-pi-lot.com/en/latest/transform/timeseries.html) filter,rotation, (https://docs.auto-pi-lot.com/en/latest/transform/geometry.html#autopilot.transform.geometry.Rotate) and aspheroid correction (https://docs.auto-pi-lot.com/en/latest/transform/geometry.html#autopilot.transform.geometry.Spheroid) to calibrate accelerometers. Then we combined it with the DLC-Live transform for a fast but accurate motion estimate from position, velocity, and acceleration measurements from three independent sensors. Since each step of the transformation is exposed in a clean API, it was straightforward to extend the Kalman filter (https://github.com/auto-pi-lot/autopilot-plugin-parallax/blob/759dbb382b90a99f71edf5070772ac18555b67dd/kalman_position.py) to accomodate the the wildly different sampling rates of the camera and IMU. It’s still got its quirks, but that’s the purpose of plugins — to make the code available and documented (https://wiki.auto-pi-lot.com/index.php/Plugin:Parallax) without formally integrating it in the library.

program structure 29

### 3.6 Stimuli

An Autopilot Tone
my_tone = sounds.Tone(
frequency = 500,
duration = 200)
my_tone.play()

Figure 3.12: Autopilot stimuli are parametrically defined and inherit all the playback logic that makes them easy to integrate in tasks

A hardware object would control a speaker, whereas stimulus objects are the individual sounds that the speaker would play. Like tasks and hardware, Autopilot makes stimulus generation portable between users, and is released with a family of common sounds like tones, noises, and sounds from files. The logic of sound presentation is contained in an inherited metaclass, so to program a new stimulus a user only needs to describe how to generate it from its parameters (Figure 3.12). Sound stimuli are better developed than visual stimuli in the current version of Autopilot, but we present a proof-of-concept visual experiment (Section 4.3) using psychopy[40]. (https://www.psychopy.org/) Autopilot controls the realtime audio server jack (http://jackaudio.org/) from an independent Python process that dumps samples directly into jack’s buffer (Figure 3.13), giving it a triggerto-playback latency very near the theoretical minimum (Section 4.1). Sounds can be pre-buffered in memory or synthesized on demand to play continuous sounds. Because the realtime server is independent from the logic of sound synthesis and storage, stimuli can be controlled independently from different threads without interrupting audio or dropping frames.
We use the Hifiberry Amp 2, (https://www.hifiberry.com/shop/boards/hifiberry-amp2/) a combined sound card and amplifier, which is capable of 192kHz/24Bit audio playback. Autopilot and Jack can output to any sound hardware, however, including the builtin audio of the Raspberry Pi if fidelity isn’t important. There are no external video cards for the Raspberry Pi, but its embedded video card is capable of presenting video and visual stimuli (Section 4.3) especially if the other computationally demanding parts of the task are distributed to other Raspberry Pis (Section 3.7). If greater video performance is needed, Autopilot is capable of running on typical desktops as well as other single-board computers with

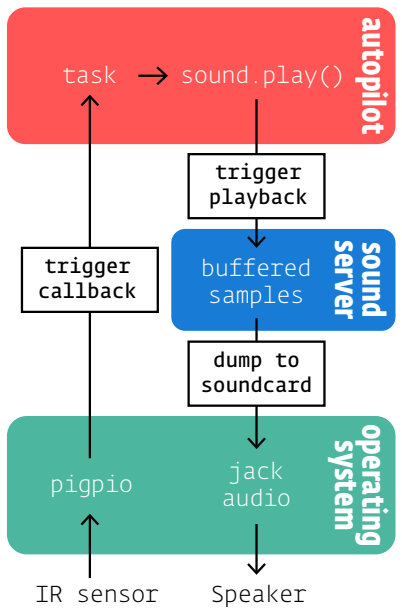
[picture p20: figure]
task; sound.play(); pigpio; operating system; trigger callback; trigger playback; jack audio; IR sensor; Speaker; buffered samples; dump to soundcard

GPUs (as we did with the Nvidia Jetson in [25]). | server sound autopilot

Figure 3.13: Our sound server keeps audio samples buffered until a .play() method is called, and then dumps them directly into the jack audio daemon.
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

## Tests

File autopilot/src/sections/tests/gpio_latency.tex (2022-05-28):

%!TEX root=../../autopilot.tex
\section{GPIO Latency}
\label{sec:gpiolatency}

Neurons compute at millisecond timescales, so any task that links neural computation to behavior needs to have near-millisecond latency. We start by characterizing Autopilot's GPIO control latency in "script mode" --- using the GPIO control classes on their own, without using any of the rest of Autopilot's modules.

\begin{margintable}[0.5cm]
\caption{GPIO Latency Materials. (Parameters in \{\} are input in separate runs)}
\label{tab:gpiomaterials}
\noindent\begin{tabularx}{\linewidth}{lX}%
\toprule
\textbf{Code} & \href{https://github.com/auto-pi-lot/plugin-paper/blob/main/plugin_paper/scripts/test_gpio.py}{test\_gpio.py} \\
\textbf{replicate} & \texttt{python test\_gpio.py -w \{0,1,2\} -n 100000}\\
\textbf{gpiozero} & \href{https://github.com/auto-pi-lot/plugin-paper/blob/main/plugin_paper/hardware/zero.py}{1.6.2} \\
\textbf{pigpio} & \href{https://github.com/sneakers-the-rat/pigpio/commit/3c237159e5995ec58cd673579bdd66a8d819b269}{3c23715} \\
\bottomrule
\end{tabularx}
\end{margintable}

\subsection{Output Latency}

We first tested the software measured latency between when a command to write a value to a GPIO pin is issued and when it completes (Figure \ref{fig:gpiolags}, Table \ref{tab:gpiomaterials}). By default, the pigpio interface we use to control GPIO pins issues a command and then confirms the request was successful by querying the pigpio daemon for the status of the pin (Write+Read). We \href{https://github.com/sneakers-the-rat/pigpio/commit/0782de06f0a5c092063118733ad2df9d65f1f1a0}{extended} pigpio to just issue the command without confirmation to estimate the true time between when the command is issued and when the voltage of the pin changes (Write). Each of these operations takes roughly 40$\mu s$ with minimal jitter (Median $\pm$ IQR --- Write Only: 40.8$\mu s \pm$0.41, Write and Read: 88.4 $\mu s \pm$2.02, n=100,000 each).

\begin{figure}[hb!]
\caption{Software latency from GPIO write to completion of command. Values are presented as medians $\pm$ IQR with n=100,000 tests for each. A random subsample of 500 (for tractability of plotting) of each type of test are presented (black points) after filtering to the bottom 99th percentile to exclude extreme outliers.  Commands sent using pigpio (red) took roughly 40$\mu s$ each (write and read are effectively two separate commands, Write Only: 40.8$\mu s \pm$0.41, Write and Read: 88.4 $\mu s \pm$2.02). The prototype gpiozero wrapper (blue) using RPi.GPIO as its backend was faster, taking 16.2$\mu s \pm$0.22 to complete.}
\label{fig:gpiolags}

\end{figure}

Pigpio is useful as a general purpose controller because of its ability to run scripts within its daemon, use hardware PWM via direct memory access, and consistently poll for pin state, but takes a latency penalty because the python interface communicates with it through a local TCP socket. To demonstrate the flexibility of Autopilot in incorporating additional software libraries, we wrote a \href{https://github.com/auto-pi-lot/plugin-paper/blob/main/plugin_tests/hardware/zero.py}{thin wrapper} around \href{https://gpiozero.readthedocs.io/en/stable/}{gpiozero}, which can use \href{https://pypi.org/project/RPi.GPIO/}{RPi.GPIO} to directly write to the GPIO registers. For simple output, this wrapper proved to be faster (16.2 $\mu s \pm 0.22$, n=100,000), and with \~63 lines of code is now available in the plugin accompanying this paper to be used, repurposed, and extended.

\subsection{Roundtrip Input/Output Latency}

\begin{margintable}[2cm]
\caption{Roundtrip Latency Materials}
\label{tab:roundtrip}
\noindent\begin{tabularx}{\linewidth}{lX}%
\toprule
\textbf{Function Generator} & \href{https://wiki.auto-pi-lot.com/index.php/Koolertron\_CJDS98}{Koolertron CJDS98} \\
\textbf{Code} & \href{https://github.com/auto-pi-lot/plugin-paper/blob/main/plugin_paper/scripts/test\_gpio.py}{test\_gpio.py} \\
\textbf{Replicate} & \texttt{python test\_gpio.py -w \{3,4\}} \\
\bottomrule
\end{tabularx}
\end{margintable}

Output commands usually aren't issued in isolation, but as a response to some external or task-driven trigger. We measured the roundtrip latency from a 5V square pulse from an external function generator to when an output pin was flipped from low to high on an oscilloscope (Table \ref{tab:roundtrip}). 

Typically that is as much methodological detail as you would expect in a scientific paper, but actually making those measurements via oscilloscope requires knowing how to set up such a test as well as how to extract the measured data afterwards --- which is not altogether trivially available technical knowledge. As an example of how integrating semantically linked documentation with experimental tools enables a fundamentally deeper kind of reproducibility and methodological transparency, we instead documented these operations, including a code sample and a guide to unlocking additional features on our oscilloscope on the \href{https://wiki.auto-pi-lot.com/index.php/Rigol\_DS1054Z}{autopilot wiki}. The code to extract traces from the oscilloscope is also included in this paper's \href{https://wiki.auto-pi-lot.com/index.php/Plugin:Autopilot\_Paper}{plugin}, which links to the oscilloscope page with a \texttt{[[Controls Hardware::Rigol DS1054Z]]} tag, so it is possible to bidirectionally find code examples from the oscilloscope page as well as find further documentation about the hardware used in this paper from the plugin page. The same can be true for any hardware used by any plugin in any paper using Autopilot.

We used the \texttt{assign\_cb} method of the \href{https://docs.auto-pi-lot.com/en/latest/hardware/gpio.html\#autopilot.hardware.gpio.Digital_In.assign_cb}{\texttt{Digital\_In}} class to test the typical roundtrip latency that Autopilot objects can deliver. This gave us a median 474 $\mu s$ (IQR: 52.5$\mu s$) latency (Red in Figure \ref{fig:gpiort}). GPIO callbacks are flexible, and can use arbitrary python functions, but if all that's needed is to trigger one pin off of another with some simple logic like a parametric digital waveform or static "on" time, pigpio also allows us to directly program pin to pin logic as a "\href{http://abyz.me.uk/rpi/pigpio/pigs.html}{pigs}" script (literally Figure \ref{fig:pigsscript}) that runs within the pigpio daemon. The pigs script gave us roughly three orders of magnitude lower latency (Median $\pm$ IQR: 370ns $\pm$ 140, blue in \ref{fig:gpiort}). 

\begin{marginfigure}[-10cm]
\begin{pythoncode*}{
label= \texttt{Pigs Trigger Script},
frame=lines,
linenos=false}
" ".join([
  "tag 999",
  # read input pin
  f"r {pin_in.pin_bcm}",
  # if off, goto 998
  f"jz 998", 
  # else, turn on
  f"w {pin_out.pin_bcm} 1",
  # then goto 999
  "jp 999", 
  "tag 998",
  # turn off
  f"w {pin_out.pin_bcm} 0",
  # jump to beginning
  f"jp 999"
])
\end{pythoncode*}
\caption{The pigs script used to trigger one pin (pin\_out), from another (pin\_in). At the expense of a little bit of complexity having to write a script in its scripting language, we are able to reduce latency by three orders of magnitude.}
\label{fig:pigsscript}
\end{marginfigure}

\begin{figure}[hb!]
\caption{Roundtrip latency from external trigger to digital output using two methods: Typical Autopilot callback function given to a \texttt{Digital\_In} object that turns a \texttt{Digital\_Out} pin on for 1ms when an input pin changes state (Red, Left, Median $\pm$ IQR: 474 $\mu s \pm$ 52.5). Pigs script that runs entirely within the pigpio daemon (Blue, Right, 380ns $\pm$ 140). For each, black points represent individual measurements (n=525), annotations are quartiles.}
\label{fig:gpiort}

\end{figure}

\clearpage

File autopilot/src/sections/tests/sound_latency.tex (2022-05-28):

%!TEX root=../../autopilot.tex
\section{Sound Latency}
\label{sec:soundlatency}

\begin{margintable}[0.3cm]
\caption{Sound Latency Materials}
\label{tab:soundmaterials}
\noindent\begin{tabularx}{\linewidth}{lX}%
\toprule
\textbf{Sound Card} & \href{https://wiki.auto-pi-lot.com/index.php/HiFiBerry_Amp2}{Hifiberry Amp2} \\
\textbf{jack} & 1.9.22 \\
\textbf{Code} & \href{https://github.com/auto-pi-lot/plugin-paper/blob/main/plugin_paper/scripts/test_sound.py}{test\_sound.py} \\
\textbf{Replicate} & \texttt{python test\_sound.py} \\
\bottomrule
\end{tabularx}
\end{margintable}

We measured end to end, hardware input to sound output latency by measuring the delay between an external digital input and the onset of a 10kHz pure tone (Table \ref{tab:soundmaterials}). Sound playback was again triggered by the \texttt{Digital\_In} class's callback method, and sound samples were buffered in a \href{https://docs.python.org/3/library/collections.html#collections.deque}{deque} held in a separate process by the jack audio client between each trial. A \texttt{Digital\_Out} pin was wired to the \texttt{Digital\_In} pin in order to deliver the trigger pulse (but the \texttt{Digital\_Out} pin was uninvolved in the software trigger for sound output).

Autopilot's \href{http://jackaudio.org/}{jack} audio backend was configured with a \texttt{192kHz} sampling rate with a buffer with two periods of of \texttt{32} samples each for theoretical minimum latency of \texttt{0.33ms}\sidenote[][-2cm]{A previous version of this paper included benchmarking and comparison to Bpod and pyControl's sound onset latency, but since then both packages have changed substantially, including Bpod creating a new \href{https://sites.google.com/site/bpoddocumentation/assembling-bpod/hifi-module}{hifi sound module} based off HiFiBerry hardware very similar to the card used here, making those benchmarks obsolete. In this version we have omitted comparative benchmarks in favor of allowing the maintainers of those packages to publish their own benchmarks.}. We observed a median 1.35ms ($\pm$ 0.72 IQR) latency across 521 samples --- roughly 4x the theoretical minimum (Figure \ref{fig:lags}). This suggests that Autopilot eliminates most perceptible end-to-end latency, which is necessary for tasks that require realtime feedback. One clear future direction is to write the sound processing loop in a compiled language exposed with a foreign function interface (FFI) to decrease both latency and jitter.

\begin{figure}[hb!]
\caption{Autopilot has a median 1.35ms ($\pm$ .72 IQR) latency between an external trigger and sound onset. Individual trials (dots, n=521) are shown beneath a density plot (red area under curve) colored by quartile (shades, numbers above are median, first, and third quartile). This latency is roughly 4x the theoretical minimum (0.33ms, dashed line).}
\label{fig:lags}

\end{figure}

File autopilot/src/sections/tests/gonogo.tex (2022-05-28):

%!TEX root=../../autopilot.tex
\section{Distributed Go/No-go Task}
\label{sec:gonogo}

\begin{margintable}[0.4cm]
\caption{Go/No-go Materials}
\label{tab:gonogomat}
\noindent\begin{tabularx}{\linewidth}{lX}%
\toprule
\textbf{Hardware} & \\
\textbf{Beam Break} & \href{https://wiki.auto-pi-lot.com/index.php/TT_Electronics_OPB901L55}{TT Electronics OPB901L55} \\
\textbf{Monitor} & \href{https://www.productchart.com/monitors/16901}{Acer S230HL} \\
\textbf{Lick Port} & \href{https://wiki.auto-pi-lot.com/index.php/Autopilot_Tripoke}{Autopilot Tripoke v1} \\
\textbf{Light Sensor} & \href{https://www.thorlabs.com/newgrouppage9.cfm?objectgroup_id=3341}{Thorlabs PM100D} \\
\midrule
\textbf{Software} & \\
\textbf{psychopy} & v3.1.5 \\
\textbf{glfw} & v1.8.3 \\
\bottomrule
\end{tabularx}
\end{margintable}{}

We designed a visual go/no-go task as a proof of concept for distributing task elements across multiple Pis, and also for the presentation of visual stimuli (Figure \ref{fig:gonogo}, Table \ref{tab:gonogomat}). While the rest of the tests presented have been re-run, in the time since the intitial publication of the preprint we have not done substantial work on Autopilot's visual stimulus module, and so this section is presented as previously written using the v0.1.0 initial release.

\begin{marginfigure}[-0cm]

\caption{Hardware distribution for the distributed go/no-go task. Red lines indicate physical connections between hardware components. The lick sensor, solenoid valve, and LED are physically bundled into one component represented as the mouse's microphone.}
\label{fig:gonogo}
\end{marginfigure}

In this task, a head-fixed subject would\sidenote{No mice were trained on this task} be running on a wheel in front of a display with a lick-detecting water port able to deliver reward. Above the port is an LED. Whenever the LED is green, if the subject drops below a threshold velocity for a fixation period, a grating stimulus at a random orientation is presented on the monitor. After a random delay, there is a chance that the grating changes orientation by a random amount. If the subject licks the port in trials when the orientation is changed, or refrains from licking when it is not, the subject is rewarded. 

One pilot controlled the operation of the task, including the coordination of a copilot. The pilot was connected to the LED and solenoid valve for reward delivery, as well as a monitor\sidenote{(\texttt{1920x1080px, 60Hz})} to display the gratings\sidenote{Visual stimuli were presented with \href{https://www.psychopy.org/}{Psychopy} using the \href{https://www.glfw.org/}{glfw} backend while Autopilot was run in a dedicated X11 server.}. The copilot continuously streamed velocity data (measured with a USB optical mouse against the surface of the wheel) back to the terminal for storage (see also Figure \ref{fig:datastreams}, which depicts the network topology for this task). The copilot waited for a message from the pilot to initiate measuring velocity, and when a rolling average of recent velocities fell below a given threshold the copilot sent a TTL trigger back to the pilot to start displaying the grating. This split-pilot topology allows us to poll the subject velocity continuously (at \texttt{125Hz} in this example) without competing for resources with psychopy's rendering engine.

We measured trigger (TTL pulse from the copilot) to visual stimulus onset latency using the measurement cursors of our oscilloscope as before. To detect the onset of the visual stimulus, we used a high-speed optical power meter attached to the top-left corner of our display monitor. The stimulus was a drifting Gabor grating drawn to fill half the horizontal and vertical width of the screen (\texttt{960 x 540px}), with a spatial frequency of \texttt{4cyc/960px} and temporal (drift) frequency of \texttt{1Hz}.

\begin{marginfigure}[-0cm]

\caption{Stacked dots are a histogram of individual observations (n=50) underneath the probability density (black line), red lines indicate quartiles.}
\label{fig:vidlat}
\end{marginfigure}

We observed a bimodal distribution of latencies (Quartiles: \texttt{28, 30, 36ms, n=50}, Figure \ref{fig:vidlat}), presumably because onsets of visual stimuli are quantized to the refresh rate (\texttt{60Hz, 16.67ms}) of the monitor. This range of latencies corresponds to the second and third frame after the trigger is sent (2/3 of observations fall in the 2nd frame, 1/3 of observations in the 3rd frame). We observed a median framerate of \texttt{36.2 FPS (IQR: 0.7)} across 50 trials (\texttt{8863} frames, Figure \ref{fig:framerate}). 

We further tested the Pi's framerate by using Psychopy's \href{https://github.com/psychopy/psychopy/blob/3.1/psychopy/demos/coder/timing/timeByFrames.py}{\texttt{timeByFrames}} test---a script that draws stimuli without any Autopilot components running---to see if the framerate limits were imposed by the hardware of the Raspberry Pi or overhead from Autopilot (Table \ref{tab:fpstests}). We tested a series of Gabor filters and \href{https://www.psychopy.org/api/visual/dotstim.html#psychopy.visual.DotStim}{random dot stimuli} (dots travel in random directions with equal velocity, default parameters) at different screen resolutions and stimulus complexities. The Raspberry Pi was capable of moderately high framerates (\texttt{>60 FPS}) for smaller, lower resolution stimuli, but struggled (\texttt{<30 FPS}) for full HD, fullscreen stimuli.

\clearpage

\begin{marginfigure}[0.5cm]

\caption{Probability density of framerates for 960 x 540px grating rendered at 1080p. Red lines indicate quartiles}
\label{fig:framerate}
\end{marginfigure}

Autopilot is appropriate for realtime rendering of simple stimuli, and the proof-of-concept API we built around Psychopy doesn't impose discernible overhead (Mean framerate for a \texttt{960 x 540px} grating at \texttt{1080p} in Autopilot: \texttt{36.2 fps}, vs. \texttt{timeByFrames}: \texttt{35.0 fps}). In the future we will investigate prerendering and caching complex stimuli in order to increase performance. A straightforward option for higher-performance video would be to deploy an Autopilot agent running on a desktop computer with a high-performance GPU, or to use a single-board computer with a GPU like the \href{https://www.nvidia.com/en-us/autonomous-machines/embedded-systems/jetson-nano/}{NVIDIA Jetson} (\$99)\sidenote[][0.3cm]{as we did in \citep{kaneRealtimeLowlatencyClosedloop2020a}}.

\begin{table}
\caption[][1cm]{Tests performed over 1000 frames with PsychoPy's \href{https://github.com/psychopy/psychopy/blob/3.1/psychopy/demos/coder/timing/timeByFrames.py}{\texttt{timeByFrames}} test.}
    \begin{tabular}{rrr|rr}
        \toprule
        \textbf{Stimulus} & \textbf{Resolution} & \textbf{Size / \# Dots}& \textbf{Mean FPS} & \textbf{$\sigma$ FPS} \\
        \midrule 
        Gabor Filter & 1280 x 720  & 300 x 300px & 106.4 & 5.5 \\
        Gabor Filter & 1920 x 1080 & 300 x 300px & 75.2 & 3.5\\
        Gabor Filter & 1280 x 720 & 640 x 360px & 53.5 & 2.2\\ 
        Gabor Filter & 1920 x 1080 & 960 x 540px & 35.0 & 1.0 \\
        Gabor Filter & 1280 x 720 & 720 x 720px & 41.5 & 2.2 \\
        Gabor Filter & 1920 x 1080 & 1080 x 1080px & 20.1 & 0.7 \\
        Random Dots & 1280 x 720 & 100 dots & 98.0 & 3.8 \\
        Random Dots & 1920 x 1080 & 100 dots & 67.6 & 3.0 \\
        Random Dots & 1280 x 720 & 1000 dots & 20.9 & 0.25 \\
        Random Dots & 1920 x 1080 & 1000 dots & 19.5 & 0.36 \\
        \bottomrule
    \end{tabular}
    \label{tab:fpstests}
\end{table}

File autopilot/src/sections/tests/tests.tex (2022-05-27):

\newthought{We have been testing and refining Autopilot} since we built our swarm of 10 training boxes in the spring of 2019. In that time 178 mice\sidenote{All procedures were performed in accordance with National Institutes of Health guidelines, as approved by the University of Oregon Institutional Animal Care and Use Committee.} have performed over 6 million trials on a range of tasks. While Autopilot is still relatively new, it is by no means untested.

In this section we will present a set of basic performance benchmarks while also showing several of the different ways that Autopilot can be used. The code for all of the following tests is available as a \href{https://github.com/auto-pi-lot/plugin-paper}{plugin} that is further documented on the \href{https://wiki.auto-pi-lot.com/index.php/Plugin:Autopilot_Paper}{wiki}, and runs on a prerelease of v0.5.0. Materials tables (Table \ref{tab:materials}) for each test link more specifically to the test code and provide additional hardware and version documentation, where appropriate.

\begin{margintable}[-0.5cm]
\caption{General Materials}
\label{tab:materials}
\noindent\begin{tabularx}{\linewidth}{lX}%
\toprule
\textbf{Hardware} & \\
Raspi & \href{https://www.raspberrypi.org/products/raspberry-pi-4-model-b/}{Raspberry Pi 4b}\\
Oscilloscope & \href{https://wiki.auto-pi-lot.com/index.php/Rigol\_DS1054Z}{Rigol DS1054Z} \\
\midrule
\textbf{Software} & \\
Autopilot & \href{https://github.com/auto-pi-lot/autopilot/tree/v0.5.0a}{v0.5.0a} \\
Plugin & \href{https://wiki.auto-pi-lot.com/index.php/Plugin:Autopilot\_Paper}{Autopilot\_Paper} \\
Python & 3.9.12 \\
RaspiOS & Bullseye \href{https://downloads.raspberrypi.org/raspios_lite_armhf/images/raspios\_lite\_armhf-2022-04-07/}{22-04-04} (lite) \\
\midrule
\textbf{Analysis} & \\
R & 4.2.0 \\
ggplot2\citep{wickhamGgplot2ElegantGraphics2016a} & 3.3.5 \\
dplyr\citep{wickhamDplyrGrammarData2022} & 1.0.9 \\
purrr\citep{henryPurrrFunctionalProgramming2020} & 0.3.4 \\
pandas\citep{mckinneyPandasFoundationalPython2011} & 1.4.2 \\
numpy\citep{waltNumPyArrayStructure2011,harrisArrayProgrammingNumPy2020a} & 1.21.6 \\ 
\bottomrule
\end{tabularx}
\end{margintable}

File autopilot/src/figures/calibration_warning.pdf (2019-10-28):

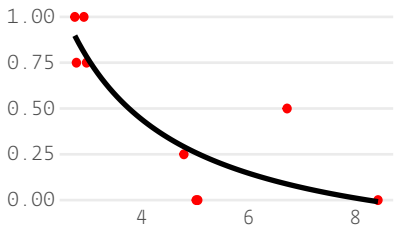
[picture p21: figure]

R

e

## ward

## Volume (uL)

## Successful Mice

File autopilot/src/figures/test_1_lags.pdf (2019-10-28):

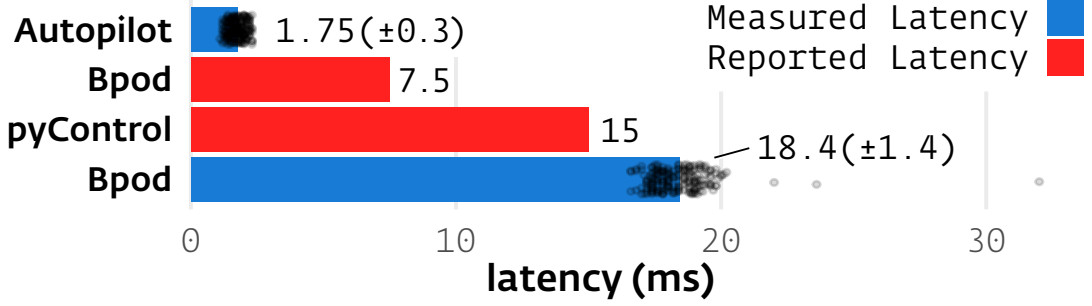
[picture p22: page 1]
Bpod; pyControl; Autopilot; latency (ms); Measured Latency Reported Latency 1.75(±0.3)

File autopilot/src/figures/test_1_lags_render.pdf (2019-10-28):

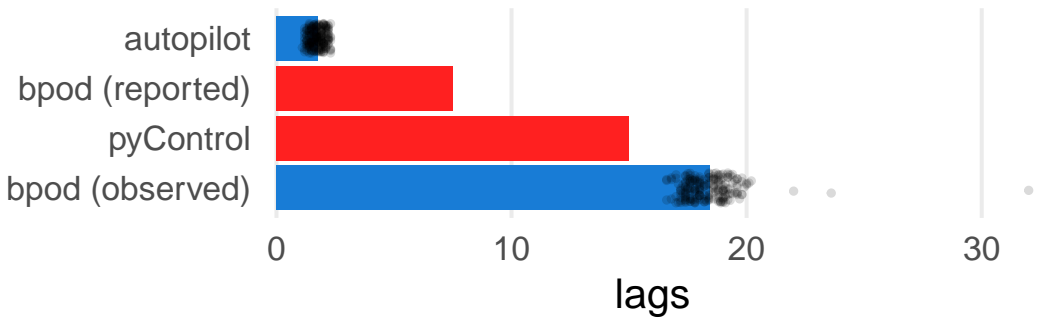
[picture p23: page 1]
bpod (observed); pyControl; bpod (reported); autopilot; lags

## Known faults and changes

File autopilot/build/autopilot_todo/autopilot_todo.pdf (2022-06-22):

## 1 Meta

- Add Lucas to authors
- add early collaborators like Chris, mackenzie, etc. who gave information and insight.
- add contribution statement
- finalize contribution statement
- add citations for bpod and pycontrol papers, i think they have come out since this!!!
- move autopilot to its own organization repository so links stay fresh! Then update the links in the paper!
- complete nosepoke and behavior box assembly instructions on wiki.
- terminal send back pilot DB to each other pilot when they connect.
- links from text to future directions
- Move go/no-go task from main autopilot library to plugin

### 1.1 Formatting

- TOC spacing!
- Smart quotes for single quotes
- Margin note positioning throughout (do at end though)
- Glossary links throughout text?
- Index???
- fix links to future directions to have correct references to individual items within list.
- add link to interface map and mapset in data model figure when docs are up

## 2 Intro

### 2.1 Foreword to Manuscript v2

- Check the changelog!

## 3 Data to Include

- Get all configuration files including chrony, prefs, etc.
- Organize and annotate data

1

## 4 Docs to write

- document the get_stream method on net_nodes!
- wiki page for the paper plugin! specifically the go no/go task

## 5 Finished

### 5.1 Preamble

- Add: Also experimental software is a missed opportunity and a strong lbockage to our ambitions of ”open science” – making an unnecessary rite of passage in struggling through behavioral setups
- This is actually a challenging technical and theoretical problem. Tension between totalizing framework and integrating many tools: autopilot tries to be mindful about both – it is a logical framework for the different parts of an experiment, allows easily hooking into each of these components, but also lets them be used separately. Autopilot was designed to play nice with other tools, but also give them a place to play nice with each other.
- ”whats missing is a glue framework”
- Reproducibility para - Mention of the wiki and plugin systems – using a linux system brings with it all a manner of technical challenges. We have designed autopilot as a system that can integrate fluid technical knowledge along with the code to use it. Also that we have designed it to let work at all stages of ”completeness” work together with its plugin framework – example with a stepper motor. thsi one might not be **exactly** what you need but it’s better than nothing.
- Note that autopilot is a continually developing system, so we don’t necessarily do everything here perfectly, many things are in progress, but this document is intended to capture the ideas that animate its development.

### 5.2 Existing Systems

- ”These are the minimum components for a complete behavior system, but there are of course many other things, means of conceptualizing and supporting. Each of these is far from monolithic and has within it a thousand design choices.”
- add transforms to ”data management”
- Update description for pyControl
- update description for BPod
- link to finite state machine section from ”pyControl uses a finite state machine”
- Bpod also has pyBpod and whatever else
- remove ”Bpod blocks operation” it’s not necessary – refocus this section on just describing the architectural decisions without including shit talking the GUI. In general, the purpose of this section is to illustrate two prior approaches to solving this problem to draw contrast with what we do differently.

2

- Can also discuss the mode by which it’s used (eg. talk about the IBL needing to make the bigass PDF) and maybe try and find some individual use cases of each that are given as examples. These are designed for individual labs to use as tools, rather than designed as a means for organizing technical knowledge within or across labs (let alone share data).

### 5.3 Limitations of existing systems

- Documentation is a big problem – don’t have low-level docs so people can inspect what’s going on. Researchers are expected to interact with it on a top-level only: the tool as is, rather than expand and hack on the library itself. Flexible tools need to have interfaces at multiple levels: yes, just use, but also be able to extend, and modify the existing system. This is an architectural, interface, and documentation question and it’s a hard one to solve!
- New Item: Community Tooling - No facility for sharing tasks, hardware development, etc. No good means of sharing practical usage advice – basically the community tooling isn’t there. Look for examples of Bpod tasks (eg. the IBL task) and how that doesn’t make for a cumulative body of knowledge. Use the christof koch quote about organization being the major problem: in order to be a force multiplier, need to be able to have peer-to-peer knowledge sharing instead of treating a piece of software as a fixed entity.
- Data - no schemas, no formal structures, sharing is hard and both take the approach that you need to write a whole additional library to analyze the data
- Devops and code tooling – Bpod stuff has no means of integrating other code because matlab doesn’t have a package manager. No CI, no tests for either Instead of this, just say that Autopilot does this
- the bottom line is that these tools weren’t designed with integration in mind, ithey might handle some subset of the experiment, but they don’t really play well with the other parts of the experiment and ultimately serve as yet another complicated node rather than something that can be compared.

## 6 Design

- We take a broad lens on reproducibility – not just good data, but a tool that integrates into a broader ecosystem of tools and reduces labor duplication beyond itself. Reproducibility is not just a question of getting everyone to upload their data, but to build the tools that make reproducibility accessible to a broader base of researchers.
- Though only the GPIO is really unique to the raspi – autopilot can be used on any unixlike system.

### 6.1 Efficiency

- integrated circuit -> microcontroller
- efficiency of interpreted languages is not the only consideration in efficiency: how easy it is to use and the time spent troubleshooting and making do with other systems is itself part of the equation, so we try and balance the ease of use witht he performance of the program

3

- Concurrency - Arguably the most radical concurrency model in autopilot is the use of multiple comptuers. So if a single processor can’t do what you want it’s trivial to have other computers running other things. This also lets different system components be isolated from one another, something that blends into the notion of agents and behavioral topologies discussed later.
- Low-Level - We make use of Python to mature an API that we will then drop down into lower level languages like C and Rust when they are stable.
- Caching - by provbiding low-level documentation, we let people choose how they want to cache – you can just hit play on a sound method or buffer it before, or generate it on the fly. You can just ‘send’ a message, or you can pre-serialize it and send it manually.

### 6.2 Flexibility

- Modularity - There is a tension between flexibiltiy and providing a complete behavioral package, to balance that we have to be very capable of keeping our code modular. We do that by implementing a sensible inheritance hierarchy with predictable and shared APIs for different objects. That way we can keep a predictable set of methods exposed while being able to modify the other
- New Section: Open Ecosystem - split apart modularity section into a discussion about being able to pick and choose different parts of the library with a new section about the choice to use the raspberry pi and a generalize dhardware approach rather than an ecosystem of specific hardware objects. Describe the wiki here?
- New Section: Plugins - replace structured expansino/code transparency section with plugin sectino. By separating local configuration files and etc. we are able to have a very flexible plugin system: users are not expected to modify files in the repository to use it (which makes it difficult to contribute later) or implement everything in a single script. instead we provide a system for expansion that scaffolds their use of the software and reuse in tasks. Expand the discussion of the task library to a general purpose pick and choose your own tool library with plugins that can be maintained by you but be part of a larger project.
- CI is also really relevant here – to make sure that it’s possible to change the system freely, we have CI and as we have been developing have been

### 6.3 Reproducibility

- New to data management section: schema stuff! We want to provide a well annotated data structure that can be exported to many different formats. To do that we have built a bunch of data modeling tools
- Update prices!

## 7 Structure

- Start by describing the hierarchical object strucutre – Autopilot is designed around a few fundamental types with abstract methods that are then elaborated. This is in progress! - how hard would it be to make this be an autogenerated figure?

4

- in this section, also talk about ability to dehydrate and rehydrate objects so they can be re-instantiated across processes and machines. - probably not necessary
- New Section: Transforms - also include DLC stuff.
- Stuff that all autopilot objects have – sick logging (give example). Autopilot is about making best practices baked into the process.
- Rename ”Children” as ”copilots” throughout

### 7.1 Tasks

- Update task header to use Pydantic models.
- end FSM section being like ”rather than trying to standardize on a particular model for tasks, we standardize on use” – We provide a set of minimal tools that can be used to write tasks, but then purposefully leave the space open for people to write them how they want, and then allow standardization to happen naturally rather than presupposing a structure and asking people to conform to it. Cite aaron swartz description of standards from his book.

### 7.2 Hardware

- Update link to refer to the wiki rather than the hardware page on autopilot website. also mention build guides and whatever. Also describe vision of being ableo to declare specific part numbers for hardware objects to be able to document the parameters of their use.
- update prices
- update figure to use new tripoke figure.
- System adaptability section seems redundant with separating task params. Abbreviate this and change this section to being about using the wiki to gather common configurations for hardware objects, benchmarks, etc. - nah just took it out.
- update system specs, if they’ve changed.

### 7.3 Stimuli

- You can also use a jetson or some other SBC with a video card if performance is more important. as we did in (cite DLC paper)
- remove stimulus and reward manager section, we don’t really have them – move this to future directions

### 7.4 Networking

- 3.8 Rewrite to say that the backbone ”station” structure is being phased out in favor of a point to point communication system. For now you can use point to point communication if timing is important, but otherwise agent-agent communication still uses the hierarchical networking structure by default.
- 3.14 remove treelike

5

### 7.5 GUI

- Change framing so we’re talking about moving the GUI towards being a visual representation of the rest of the data modeling systems, so that different components of the system automatically get interfaces. Decoupling all the logic of the GUI into general system methods that the GUI can just visually present.
- We’re going to change the plotting stuff to be built into the data description, but for now it’s independent.

## 8 Tests

- Functionality testing is done in our CI, so these are just rough performance characterizations that can always change. So as much as it doesn’t make sense to publish performance characterization in a static paper, we’ll do some of that here
- Add version numbers to each of the test in margin note.
- Update language on tests. We have been working on autopilot continuously, # commits have happened, etc.
- Remove Bpod comparison tests. too messy. Then also remove language at the top that we improve efficiency an order of magnitude
- CODE: replace JSON with msgpack.
- Re-run all tests

– Sound latency
– Network latency
– Network throughput
- Make sure to actually NTP sync!
- NEW Tests

– GPIO on/off latency
– networked GPIO on/off latency
– Camera FPS for picam/FLIR cam?
– timed GPIO on/off jitter.
- Just say we haven’t done any work on visual stimuli so this test was run with the release version of autopilot.

6

## 9 Future Directions

- RDF export, linked data capabilities between the wiki and data structures
- Also working on a related ingest project to be able to automatically bring in data from other sources made during use.
- Unify slot, signal, and trigger architecture to make different pieces more effortlessly compatible.
- Write rust interface to GPIO pins
- New Section: Knowledge Organization - We will continue to explore additional avenues for improving the interfaces with which we share information. If there’s anything we’ve learned over the past few years it’s that technical profiency isn’t enough: you need to support a community of people around the tool and make sure they have the means of answering questions for themselves. There is a ton of additional informatino that’s needed to perform any experiment that doesn’t fit neatly in code or docs, hence the wiki! To make things both technically reproducible AND practically reproducible, the plugin system is built into a semantic wiki that can organize structured data (wiki stuff here for sure, not in the other place i said)
- pipelining for transforms, forking and branching to be able to get intermediate products out as well as merge multiple pipes, as well as different transformatino rhythms that let you control more finely how transformatino piplines behave
- stimulus managers - in a previous version we described these, thinking that they would be developed shortly. we still haven’t gotten around to that but have left stubs in place.
- granular dependency management!
- agent management! make it easier to deploy and configure pilots from a single place

### 9.1 Data

- (In program design section) - Change standardized task decriptions to being about schemas. Tasks and data use a shared representation (along with the subject class) that lets you export descrptions as JSON, but also into NWB and etc.
- (In program design section) - Self-documenting data -> be more explicit that we record everything
- Annotate code example

### 9.2 Agents

- Remove child agent.
- talk about managing dependencies for particular types of agents here, more relevant than terminal vs. pilot etc.
- Talk about scripts and system configuration here.
- Change child figure to being one with multiple copilots

7

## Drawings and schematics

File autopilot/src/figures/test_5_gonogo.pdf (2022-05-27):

+ +

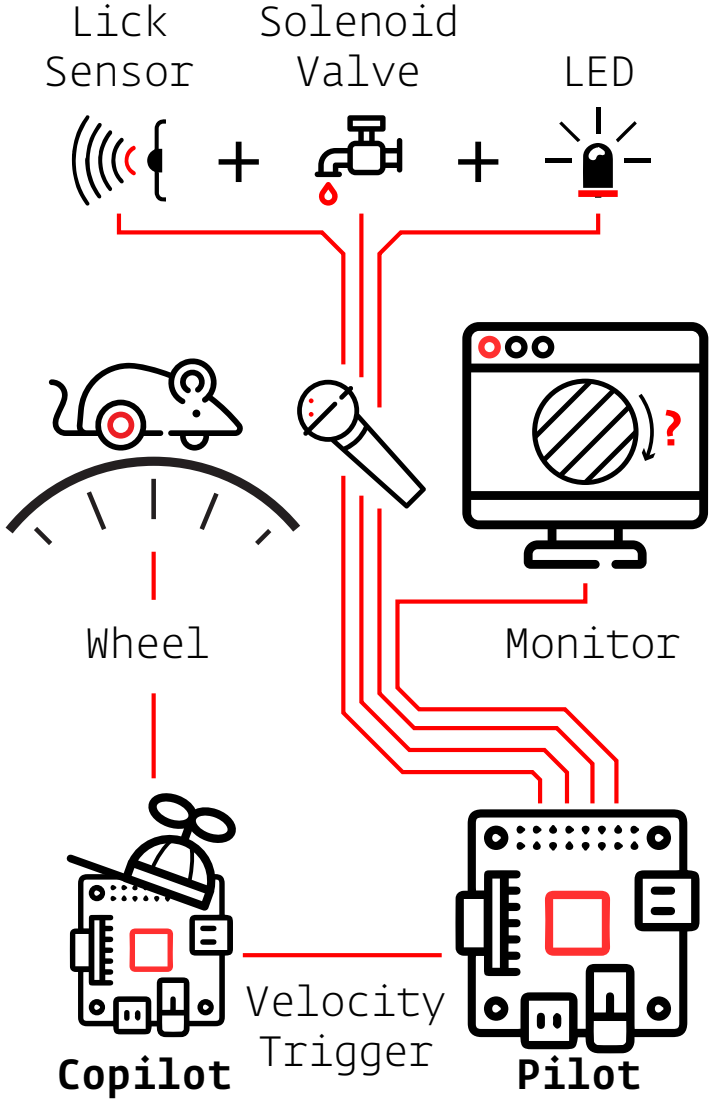
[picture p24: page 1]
Wheel; LED; Monitor; Lick Sensor; Solenoid Valve; Velocity; Trigger Copilot; Pilot

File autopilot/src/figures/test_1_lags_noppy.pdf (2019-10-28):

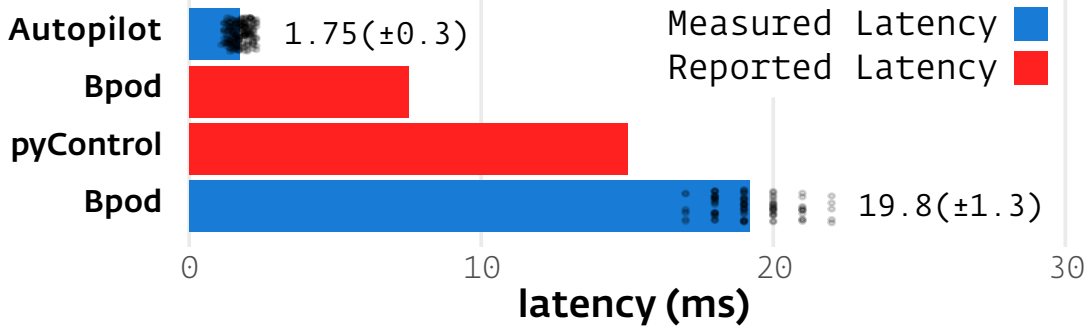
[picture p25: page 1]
Bpod; pyControl; Autopilot; latency (ms); Measured Latency Reported Latency

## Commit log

2022-04-05 initial move
    [blueprint.blend, nosepoke_lowpoly.stl, porthole_lowpoly.stl]
2022-05-03 starting writing tests section
    [autopilot_latency_082019.csv, bpod_latency_xonar.csv, pycontrol_poke.xlsx, roundtrip_pigs_script.csv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]
2022-05-10 still working on tests, just finished sound
    [22-05-02T19-10-00_sound-latency_extracted.csv, sound-latency_192k_n2_p32_0_extracted.csv]
2022-05-11 finished network tests
    [1000_10pis_0size.csv, 1000_1pis_0size.csv, 1000_2pis_0size.csv, 1000_2pis_paylode.csv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]
2022-05-12 at the future directions
    [bw_preserialized.csv]
2022-05-14 before materials
2022-05-17 cleaning up materials
2023-12-01 rename frame_test_2 data to strip colons for windows compability
    [frameintervals_2019-08-29T19-33-03.csv, frameintervals_2019-08-29T19-33-13.csv, frameintervals_2019-08-29T19-33-24.csv, frameintervals_2019-08-29T19-33-34.csv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]
